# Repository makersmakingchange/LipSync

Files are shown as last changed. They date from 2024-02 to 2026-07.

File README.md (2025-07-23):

# LipSync

The LipSync is a mouth-operated sip-and-puff joystick that can emulate a mouse, wireless Bluetooth mouse, or gamepad. It enables people with disabilities that limit their mobility to control a computer, gaming console, smart phone, or tablet.

This most recent version, the LipSync 4.1, is made up of the LipSync Joystick and LipSync Hub. The Joystick is the primary user interface, and contains a low-force Hall-Effect joystick and sip and puff sensors. The Hub has a display that provides a graphical interface for independently adjusting settings, as well as it provides the connection to the host device and up to three external assistive switches with 3.5 mm jacks.

The device is comprised of off-the-shelf electronics and hardware, a custom PCB and 3D printed parts. The overall cost of materials (including materials required in bulk) for a single build is about $325 (plus shipping). In larger quantities, the cost of materials is closer to $175.

The LipSync is compatible with a range of host devices that are able to support a USB Mouse, a USB Gamepad and/or a Bluetooth Mouse. Compatible devices include PC and Mac computers and laptops, Android, iOS, and Windows smartphone and tablets, and the Xbox Adaptive Controller. 

The LipSync is Open Assistive Technology (OpenAT) and is certified as Open Source Hardware by the Open Source Hardware Association under the OSHWA UID [CA000046](https://certification.oshwa.org/ca000046.html). Under the terms of the open source hardware licenses, the LipSync may be built, used, and improved by anyone.  

Older versions of the LipSync are now obsolete. Documentation and design files are still available at the [LipSync Classic Repository.](https://github.com/makersmakingchange/OldLipSync)

The existing LipSync Interface Cable options in the BOM are not in stock. We are working on sourcing suitable alternatives.

Last updated: 2025-Jul-22

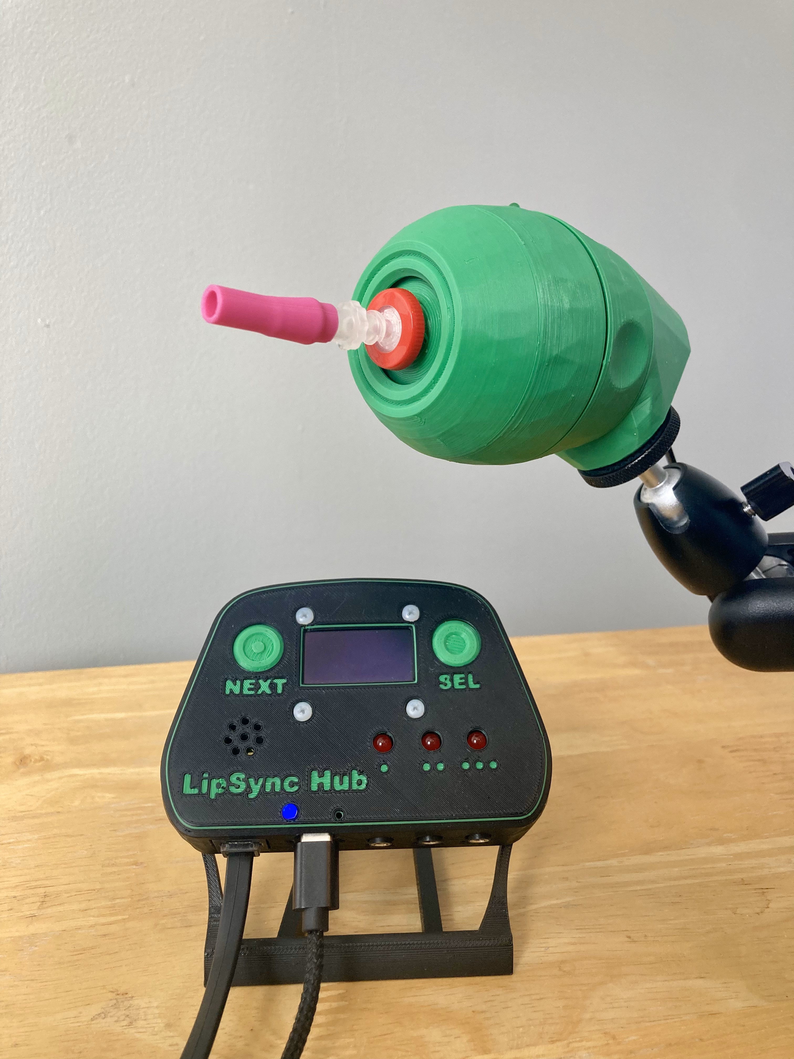
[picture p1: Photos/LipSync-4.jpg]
A green 3D-printed LipSync joystick with a pink sip-and-puff tube is mounted on an adjustable black arm. In front of it sits the LipSync Hub, a black and green control box with a small display screen, labeled buttons ('NEXT' and 'SEL'), indicator lights, and a USB cable connected at the bottom. Bot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


Makers Making Change Assistive Device Library Listing: [https://www.makersmakingchange.com/s/product/LipSync](https://www.makersmakingchange.com/s/product/lipsync/01tJR000000698fYAA)

## OpenAT Joysticks
This design is part of the [OpenAT Joystick Project](https://github.com/makersmakingchange/OpenAT-Joysticks), a collection of open source designs for digital access and adapted gaming. 

## How to Obtain the Device
### 1. Do-it-Yourself (DIY) or Do-it-Together (DIT)

This is an open-source assistive technology, so anyone is free to build it. All of the files and instructions required to build the device are contained within this repository. Refer to the Maker Guide below.

### 2. Request a build of this device

You may also submit a build request through the [MMC Library Page](https://www.makersmakingchange.com/s/product/LipSync/<mmc-salesforce-id>) to have a volunteer maker build the device. As the requestor, you are responsible for reimbursing the maker for the cost of materials and any shipping.

### 3. Build this device for someone else

If you have the skills and equipment to build this device, and would like to donate your time to create the device for someone who needs it, visit the [MMC Maker Wanted](https://makersmakingchange.com/maker-wanted/) section.

## Build Instructions

### 1. Read through the Maker Guide

The [Maker Guide](/Documentation/LipSync_Maker_Guide.pdf) contains all the necessary information to build this device, including tool lists, assembly instructions, programming instructions and testing instructions.

### 2. Order the Off-The-Shelf Components

The [Bill of Materials](/Documentation/LipSync_BOM.csv) lists all of the parts and components required to build the device. 

### 3. Print the 3D Printable components

All of the files and individual print files can be in the [/Build_Files/3D_Printing_Files](/Build_Files/3D_Printing_Files/) folder.

### 4. Assemble the LipSync

Reference the Assembly Guide section of the [Maker Guide](/Documentation/LipSync_Maker_Guide.pdf) for the tools and steps required to build each portion.

## How to improve this Device
As open source assistive technology, you are welcomed and encouraged to improve upon the design. 

## Files
### Documentation
| Document             | Version | Link                                                                     | Notes             |
|----------------------|---------|--------------------------------------------------------------------------|-------------------|
| Design Rationale     | 4.1     | [LipSync_Design_Rationale](/Documentation/LipSync_Design_Rationale.pdf)  |                   |
| Maker Guide          | 4.1     | [LipSync_Maker_Guide](/Documentation/LipSync_Maker_Guide.pdf)            |                   |
| Bill of Materials    | 4.1     | [LipSync_Bill_of_Materials](/Documentation/LipSync_BOM.csv)              |                   |
| User Guide           | 4.1     | [LipSync_User_Guide](/Documentation/LipSync_User_Guide.pdf)              |                   |
| Quickstart Guide     | 4.1     | [LipSync_Quickstart_Guide](/Documentation/LipSync_Quickstart_Guide.pdf)  |                   |
| Changelog            | 4.1     | [LipSync_Changelog](CHANGES.txt)                                         |                   |

### Design Files
 - [CAD Files](/Design_Files/CAD_Design_Files)
 - [PCB Files](/Design_Files/PCB_Design_Files)

### Build Files
 - [3D Printing Files](/Build_Files/3D_Printing_Files/)
 - [PCB Files](/Build_Files/PCB_Build_Files/)
 - [Firmware Files](/Build_Files/Firmware_Files)

## License
Copyright (c) 2024-2025 Neil Squire / Makers Making Change.

This repository describes Open Hardware:
 - Everything needed or used to design, make, test, or prepare the LipSync is licensed under the [CERN 2.0 Weakly Reciprocal license (CERN-OHL-W v2) or later](https://cern.ch/cern-ohl ) .
 - All software is under the [GNU General Public License v3.0 (GPL-3.0)](https://www.gnu.org/licenses/gpl.html).
 - Accompanying material such as instruction manuals, videos, and other copyrightable works that are useful but not necessary to design, make, test, or prepare the LipSync are published under a [Creative Commons Attribution-ShareAlike 4.0 license (CC BY-SA 4.0)](https://creativecommons.org/licenses/by-sa/4.0/) .

You may redistribute and modify this documentation and make products using it under the terms of the [CERN-OHL-W v2](https://cern.ch/cern-ohl).
This documentation is distributed WITHOUT ANY EXPRESS OR IMPLIED WARRANTY, INCLUDING OF MERCHANTABILITY, SATISFACTORY QUALITY AND FITNESS FOR A PARTICULAR PURPOSE.
Please see the CERN-OHL-W v2 for applicable conditions.

Source Location: https://github.com/makersmakingchange/LipSync

List of open source licenses. Hardware: CERN-OHL-W-2.0, Software: GPL-3.0-or-later, Documentation: CC-BY-SA-4.0.

## Attribution

The LipSync was designed by Neil Squire Society / Makers Making Change. The initial development of a 3D printable LipSync was supported by the Google Impact Challenge: Disabilities grant from Google.org. Further development was supported through the Government of Canada's Innovation Science and Economic Development [Accessible Technology Program](https://ised-isde.canada.ca/site/accessible-technology-program). These and other funders have also enabled Neil Squire / Makers Making Change to deploy numerous LipSyncs to users at reduced cost.

The latest design (V4.0) incorporates feedback and suggestions from numerous users, clinicians, and volunteer makers. In particular, 4.0.AlphaII was tested by the following users: Omar Al-azawi, Don Danbrook, Ean Price, Jim Ryan and Kaileen Selig.

V4.0 incorporates several commercially available open source hardware components:
 - [Adafruit TLV493D Triple-Axis Magnetometer - STEMMA QT / Qwiic](https://www.adafruit.com/product/4366). The PCB design is available under a CC-BY-SA 4.0 license at https://github.com/adafruit/Adafruit-TLV493D-PCB. 
 - [Adafruit LPS33HW Water Resistant Pressure Sensor - STEMMA QT](https://www.adafruit.com/product/4414). The PCB design is available under a CC-BY-SA 4.0 license at https://github.com/adafruit/Adafruit-LPS3X-PCB. 
 - [Adafruit LPS22 Pressure Sensor - STEMMA QT / Qwiic - LPS22HB](https://www.adafruit.com/product/4633). The PCB design is available under a CC-BY-SA 4.0 license at https://github.com/adafruit/Adafruit-LPS2X-PCB. 
 - [Adafruit 128X64 monochrome OLED Display Board](https://www.adafruit.com/product/938). The PCB design is available under a CC-BY-SA 4.0 license at https://github.com/adafruit/Adafruit-128x64-Monochrome-OLED-PCB.
 - [SparkFun Qwiic Adapter Board (DEV-14495)](https://www.sparkfun.com/products/14495). The PCB design is available under a CC-BY-SA 4.0 license at https://github.com/sparkfun/Qwiic_Adapter.   
 - [SparkFun RJ11 Breakout Board (BOB-14021)](https://www.sparkfun.com/products/14021). The PCB design is available under a CC-BY-SA 4.0 license at https://github.com/sparkfun/RJ11_Breakout. 

The LipSync firmware utilizes the Arduino development platform, an open-source electronics platform based on easy-to-use hardware and software. Arduino is developed and maintained by the Arduino community, and the project wouldn't be possible without their contributions.
Arduino is a registered trademark of Arduino AG. For more information about Arduino and to contribute to the community, visit the official Arduino website at www.arduino.cc.
The LipSync Firmware code uses several libraries:
 - [Adafruit_BusIO](https://github.com/adafruit/Adafruit_BusIO)  by Adafruit
 - [Adafruit_GFX](https://github.com/adafruit/Adafruit-GFX-Library) by Adafruit
 - [Adafruit_LPS2X](https://github.com/adafruit/Adafruit_LPS2X) by Adafruit
 - [Adafruit_LPS33HW](https://github.com/adafruit/Adafruit_LPS35HW) by Adafruit
 - [Adafruit_Sensor](https://github.com/adafruit/Adafruit_Sensor) by Adafruit
 - [Adafruit_SSD1306](https://github.com/adafruit/Adafruit_SSD1306) by Adafruit
 - [ArduinoJson](https://github.com/bblanchon/ArduinoJson) by Benoit Blanchon
 - [TLV493D-A1B6](https://github.com/Infineon/TLV493D-A1B6-3DMagnetic-Sensor) by Infineon Technologies

### Contributors
Designers:
 
 - Derrick Andrews, Neil Squire Society / Makers Making Change.
 - Stephan Dobri, Neil Squire Society / Makers Making Change.
 - Tyler Fentie, Neil Squire Society / Makers Making Change.
 - Milad Hajihassan, Neil Squire Society / Makers Making Change.
 - Jake McIvor, Neil Squire Society / Makers Making Change.
 - Stephen Moyer, Neil Squire Society / Makers Making Change.
 - Brad Wellington, Neil Squire Society / Makers Making Change.
 - Josie Versloot, Neil Squire Society / Makers Making Change.
 
## Open Source Hardware Certification

The LipSync has been certified as open source hardware by the Open Source Hardware Association under the OSHWA UID [CA000046](https://certification.oshwa.org/ca000046.html).

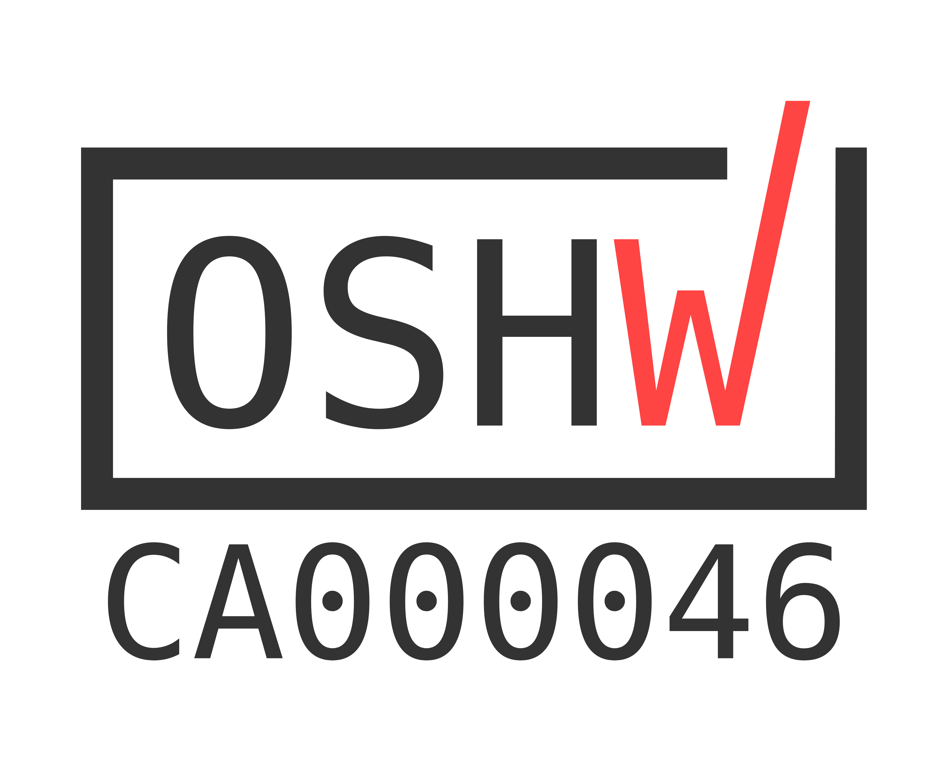
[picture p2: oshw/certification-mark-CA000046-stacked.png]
Open Source Hardware Certification Mark for LipSync: CA000046


---

## About Makers Making Change
[Makers Making Change Logo](https://www.makersmakingchange.com/)

Makers Making Change is a program of [Neil Squire](https://www.neilsquire.ca/), a Canadian non-profit that uses technology, knowledge, and passion to empower people with disabilities.

Makers Making Change leverages the capacity of community based Makers, Disability Professionals and Volunteers to develop and deliver affordable Open Source Assistive Technologies.

 - Website: [www.MakersMakingChange.com](https://www.makersmakingchange.com/)
 - GitHub: [makersmakingchange](https://github.com/makersmakingchange)
 - Twitter: [@makermakechange](https://twitter.com/makermakechange)
 - Instagram: [@makersmakingchange](https://www.instagram.com/makersmakingchange)
 - Facebook: [makersmakechange](https://www.facebook.com/makersmakechange)
 - LinkedIn: [Neil Squire Society](https://www.linkedin.com/company/neil-squire-society/)
 - Thingiverse: [makersmakingchange](https://www.thingiverse.com/makersmakingchange/about)
 - Printables: [MakersMakingChange](https://www.printables.com/@MakersMakingChange)

### Contact Us
For technical questions, to get involved, or to share your experience we encourage you to [visit our website](https://www.makersmakingchange.com/) or [contact us](https://www.makersmakingchange.com/s/contact).

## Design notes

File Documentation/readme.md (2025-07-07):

This folder contains the documentation for the LipSync. Editable versions of the documentation are located in the [Working_Documents](Documentation/Working_Documents) folder.

# Quick Links
Arduino IDE Board files for Seeed XIAO nRF52840: https://files.seeedstudio.com/arduino/package_seeeduino_boards_index.json

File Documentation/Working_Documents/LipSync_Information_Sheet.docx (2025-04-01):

# Contents

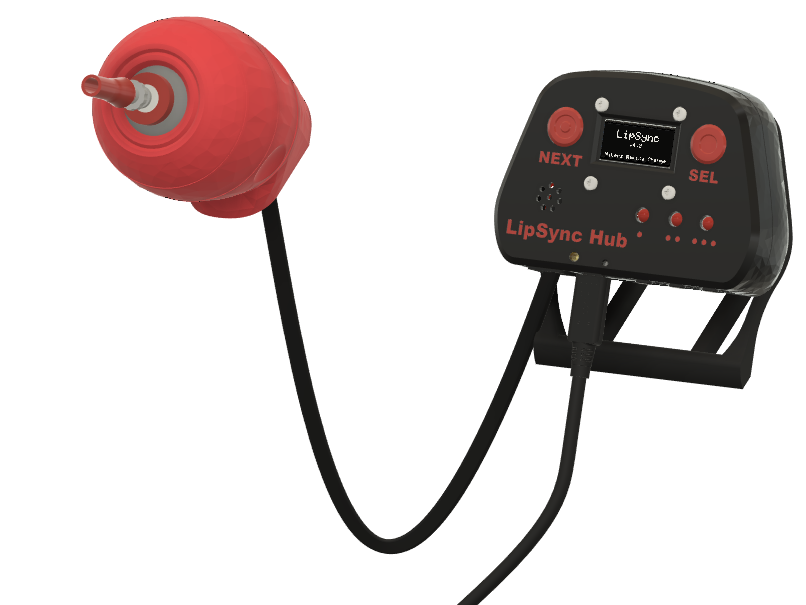
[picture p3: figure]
Numbered diagram of LipSync Setup
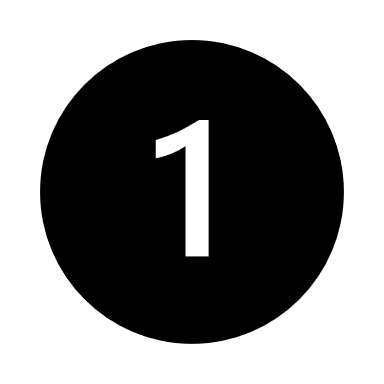
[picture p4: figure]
Badge 1 with solid fill
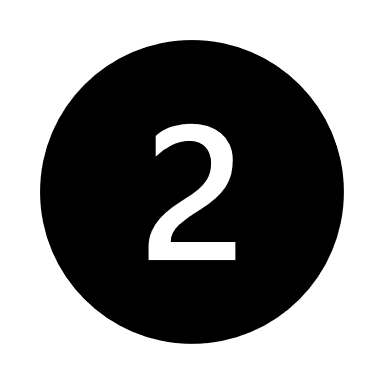
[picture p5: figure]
Badge with solid fill
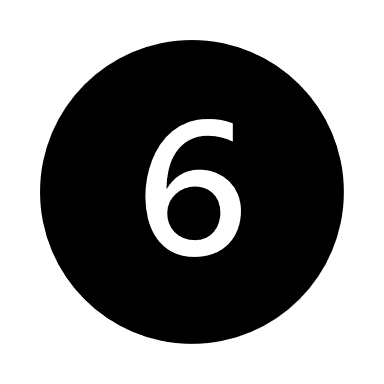
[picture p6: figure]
Badge 6 with solid fill
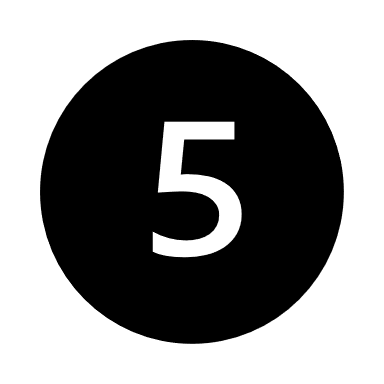
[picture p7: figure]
Badge 5 with solid fill
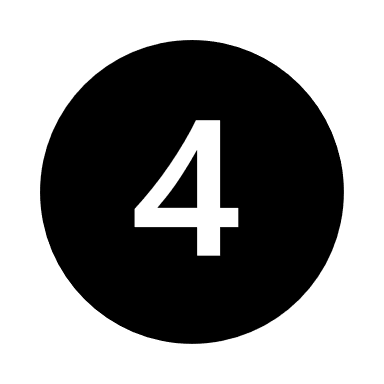
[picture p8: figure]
Badge 4 with solid fill
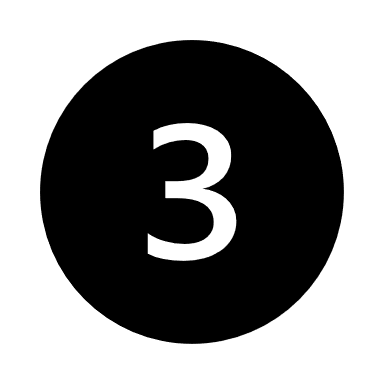
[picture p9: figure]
Badge 3 with solid fill

ID Part QTY 1 LipSync Joystick 1 2 LipSync Hub 1 3 LipSync Interface Cable 1 4 LipSync Hub Stand 1 5 LipSync Mouthpieces 5 6 USB-C – USB-A Cable 1

# Setup Instructions

1. Mount the LipSync Joystick.
2. Mount the Hub on the Hub Stand.
3. Connect the Joystick to the Hub using the Interface Cable.
4. Attach a mouthpiece to the Joystick.
5. Connect the Hub to the Host Device using a USB Cable.

# Additional Documentation

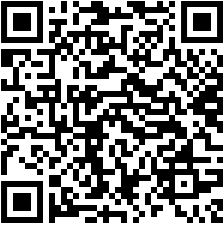
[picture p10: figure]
LipSync Quickstart Guide PDF QR Code
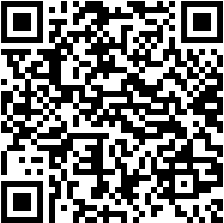
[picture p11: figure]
LipSync User Guide PDF QR Code

Quickstart Guide (https://github.com/makersmakingchange/LipSync/blob/main/Documentation/LipSync_Quickstart_Guide.pdf) | User Guide (https://github.com/makersmakingchange/LipSync/blob/main/Documentation/LipSync_User_Guide.pdf)

© 2024-2025 Neil Squire Society. This work is licensed under the CC BY SA 4.0 License: http://creativecommons.org/licenses/by-sa/4.0 Files available at https://github.com/makersmakingchange/LipSync Page 1 of 1

V4.1 | MARCH 2025 LipSync INFORMATION SHEET

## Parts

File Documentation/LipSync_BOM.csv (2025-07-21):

 | LipSync |  |  |  |  |  |  | Total filament (g) |  |  | Unit Cost | Total Cost | Total Print time (hr)
 | Version: | 4.1 |  | Last updated: | 2025-Mar-21 |  |  | 158 |  |  | $176.11 | $295.70 | 15:03
 | Commercial Parts
ID | Part | Description |  | Manufacturer | Supplier | Supplier PN | QTY | QTY / PKG | PKGs | $/PKG | Price per Unit | Total Price |  | Link | Alternate
Joystick Parts
U2 | TLV493D | Adafruit TLV493D Triple-Axis Magnetometer - STEMMA QT / Qwiic | Joystick | Adafruit | Digikey | 1528-4366-ND | 1 | 1 | 1 | $8.53 | $8.53 | $8.53 |  | https://www.digikey.ca/en/products/detail/adafruit-industries-llc/4366/10481837
U3 | LPS33HW | Adafruit LPS33HW Water Resistant Pressure Sensor - STEMMA QT | Joystick | Adafruit | Digikey | 1528-4414-ND | 1 | 1 | 1 | $17.91 | $17.91 | $17.91 |  | https://www.digikey.ca/en/products/detail/adafruit-industries-llc/4414/11201428
U4 | LPS22 | Adafruit LPS22 Pressure Sensor - STEMMA QT / Qwiic - LPS22HB | Joystick | Adafruit | Digikey | 1528-4633-ND | 1 | 1 | 1 | $9.96 | $9.96 | $9.96 |  | https://www.digikey.ca/en/products/detail/adafruit-industries-llc/4633/12396897
BRG | Bearing | 0.250" ball bearing, 1/4" ID, 0.5" OD | Joystick | Mechatronics Bearing Group | Digikey | 1995-1003-ND | 4 | 1 | 4 | $3.41 | $13.64 | $13.64 |  | https://www.digikey.ca/en/products/detail/mechatronics-bearing-group/DDRI814ZZRA3P25LY121/9608362
MAG | Magnet | Cylindrical magnet, 8 mm OD, 2.5 mm thick | Joystick | Radial Magnet, Inc. | Digikey | 469-1029-ND | 3 | 1 | 3 | $1.18 | $3.54 | $3.54 |  | https://www.digikey.ca/en/products/detail/radial-magnets-inc/9029/5218824
CBL-QWIIC-150-M | QWIIC-150 to Male Headers | JST SH 4-PIN TO PREMIUM MALE HEA | Joystick | Adafruit | Digikey | 1528-4209-ND | 1 | 1 | 1 | $1.39 | $1.39 | $1.39 |  | https://www.digikey.ca/en/products/detail/adafruit-industries-llc/4209/10230003
CBL-QWIIC-50 | QWIIC-50 | Qwiic JST SH 4-pin Cable - 50mm | Joystick | SparkFun Electronics | Digikey | 1568-PRT-17260-ND | 1 | 1 | 1 | $1.52 | $1.52 | $1.52 |  | https://www.digikey.ca/en/products/detail/sparkfun-electronics/PRT-17260/13629028
CBL-QWIIC-200 | QWIIC-200 | Qwiic Cable JST SH 4-pin Cable - 200mm | Joystick | SparkFun Electronics | Digikey | 1568-PRT-17258-ND‎ | 1 | 1 | 1 | $2.48 | $2.48 | $2.48 |  | https://www.digikey.ca/en/products/detail/sparkfun-electronics/PRT-17258/13629029?s=N4IgTCBcDaIAoCUAqBaAjAdjAVgBwgF0BfIA
PCB2 | RJ11 Breakout board | RJ11 Breakout | Joystick | SparkFun Electronics | Digikey | 1568-1440-ND | 1 | 2 | 1 | $3.01 | $1.51 | $3.01 |  | https://www.digikey.ca/en/products/detail/sparkfun-electronics/BOB-14021/6228638
CBL-RJ11 | RJ11 cable | Modular Cable Plug to Plug 6p6c (RJ11, RJ12, RJ14, RJ25) 7.00' (2.13m) Unshielded | Joystick Cable | Assmann WSW Components | Digikey | A2662R-07-ND | 1 | 1 | 1 | $3.94 | $3.94 | $3.94 |  | https://www.digikey.ca/en/products/detail/assmann-wsw-components/AT-S-26-6-6-B-7-R/1972588
J1 | Modular Connector Jack | Jack Modular Connector 6p6c (RJ11, RJ12, RJ14, RJ25) 90° Angle (Right) Unshielded Cat3 | Joystick | TE Connectivity AMP Connectors | Digikey | A31422-ND | 2 | 1 | 2 | $1.45 | $2.90 | $2.90 |  | https://www.digikey.ca/en/products/detail/te-connectivity-amp-connectors/5555165-1/769566
- | Male Luer Connectors | Mouthpiece Connector to Gimbal | Joystick |  | Amazon | B13193 | 1 | 30 | 1 | $11.99 | $0.40 | $11.99 |  | https://www.amazon.ca/gp/product/B0B8CJVX3S
- | Silicone Tubing, 2 mm ID, 4 mm OD | Air path to sensor | Joystick |  | Amazon |  | 50 | 3000 | 1 | $12.49 | $0.21 | $12.49 |  | https://www.amazon.ca/gp/product/B01C3GCZTM
Hub Parts
CBL-QWIIC-100 | QWIIC-100 | Qwiic JST SH 4-pin Cable - 100 mm | Hub | Adafruit | Digikey | 1528-4210-ND | 1 | 1 | 1 | $1.39 | $1.39 | $1.39 |  | https://www.digikey.ca/en/products/detail/adafruit-industries-llc/4210/10230021
U1 | Seeed Studio Xiao nrf52840 | Microcontroller | Hub | Seeed Studio Technology Co., Ltd. | Digikey | 1597-102010448-ND | 1 | 1 | 1 | $15.85 | $15.85 | $15.85 |  | https://www.digikey.ca/en/products/detail/seeed-technology-co.,-ltd/102010448/16652893
J6 | Male Headers for Xiao | 7-pin male headers for microcontroller | Hub | Seeed Studio Technology Co., Ltd. | Digikey | 1597-102010490-ND | 2 | 5 | 1 | $0.37 | $0.15 | $0.37 |  | https://www.digikey.ca/en/products/detail/seeed-technology-co-ltd/102010490/19176770
SW1/SW2/SW3 | Mono Switch Jacks | Mono switch jacks | Hub | CUI Devices | Digikey | CP1-3535NG-ND | 3 | 1 | 3 | $2.29 | $6.87 | $6.87 |  | https://www.digikey.ca/en/products/detail/cui-devices/SJ1-3535NG/738699
S1/S2 | Tactile switches | Tactile switches for controls | Hub | Omron | Digikey | SW801-ND | 2 | 1 | 2 | $1.02 | $2.04 | $2.04 |  | https://www.digikey.ca/en/products/detail/omron-electronics-inc-emc-div/B3F-5050/368377
J5 | 7 Pin Female Headers | 7 position female headers | Hub | Sullins Connector Solutions | Digikey | S7005-ND | 2 | 1 | 2 | $0.88 | $1.76 | $1.76 |  | https://www.digikey.ca/en/products/detail/sullins-connector-solutions/PPTC071LFBN-RC/810146
J2 | 4 Pin Male Headers | 4 Pin Male Headers | Hub | Sullins Connector Solutions | Digkey | S1011EC-04-ND | 1 | 1 | 1 | $0.19 | $0.19 | $0.19 |  | https://www.digikey.ca/en/products/detail/sullins-connector-solutions/PRPC004SAAN-RC/2775250
DISP | LCD feedback screen | Monochrome 1.3" 128x64 OLED graphic display - STEMMA QT / Qwiic | Hub | Adafruit | Digikey | 1528-1512-ND | 1 | 1 | 1 | $30.47 | $30.47 | $30.47 |  | https://www.digikey.ca/en/products/detail/adafruit-industries-llc/938/5774238
LS1 | Buzzer PS1240 | Piezo Buzzer PS1240 | Hub | TDK | Digikey | 445-2525-1-ND - Cut Tape (CT) | 1 | 1 | 1 | $0.92 | $0.92 | $0.92 |  | https://www.digikey.ca/en/products/detail/tdk-corporation/PS1240P02BT/935924
D1/D2/D3 | 5MM Red LED | Diffused 5MM Round T/H Red LED | Hub | Würth Elektronik | Digikey | 732-5016-ND | 3 | 1 | 3 | $0.26 | $0.78 | $0.78 |  | https://www.digikey.ca/en/products/detail/w%C3%BCrth-elektronik/151051RS11000/4490012
R2/R3/R4 | LED Resistors | 68 Ohm Resistor, 1/4W | Hub | YAGEO | Digikey | 68QBK-ND | 3 | 1 | 3 | $0.16 | $0.48 | $0.48 |  | https://www.digikey.ca/en/products/detail/yageo/CFR-25JB-52-68R/2832
R1 | Speaker Resistor | 100 Ohm Resistor | Hub | YAGEO | Digikey | 100XBK-ND | 1 | 1 | 1 | $0.14 | $0.14 | $0.14 |  | https://www.digikey.ca/en/products/detail/yageo/MFR-25FBF52-100R/12795
C1 | Capacitor | 10 µF Ceramic Capacitor | Hub | KEMET | Digikey | C430C106K3R5TA-ND | 1 | 1 | 1 | $1.01 | $1.01 | $1.01 |  | https://www.digikey.ca/en/products/detail/kemet/C430C106K3R5TA/6685941
J4 | Qwiic Adapter Board | Sparkfun Qwiic Adapter | Hub | SparkFun Electronics | Digikey | 1568-1785-ND | 1 | 1 | 1 | $2.34 | $2.34 | $2.34 |  | https://www.digikey.ca/en/products/detail/sparkfun-electronics/DEV-14495/7942483
M2.5n | M2.5 Nut | HEX NUT, NATURAL, NYLON, M2.5 X | Hub + Joystick | Essentra Components | Digikey | 04M025045HN | 7 | 1 | 7 | $0.19 | $1.33 | $1.33 |  | https://www.digikey.ca/en/products/detail/essentra-components/04M025045HN/9677099
M2.5x8 | M2.5 Screw - 8 mm length | PAN PHILLIPS SCREW, M2.5X0.45 T x 8 mm Long | Hub + Joystick | Essentra Components | Digikey | 50M025045P008 | 7 | 1 | 7 | $0.20 | $1.40 | $1.40 |  | https://www.digikey.ca/en/products/detail/essentra-components/50M025045P008/11638585
LP | Light Pipe 0.250" | Light Pipe | Hub + Joystick | Dialight | Digikey | 350-3746-ND | 2 | 1 | 2 | $1.66 | $3.32 | $3.32 |  | https://www.digikey.ca/en/products/detail/dialight/51513030250F/4965201
No4x3_8 | No.4 Screw x 3/8in | SHT MTL SCREW PAN PHIL #4 | Hub + Joystick | Serpac | Digikey | SR6005-ND | 8 | 1 | 8 | $0.63 | $5.04 | $5.04 |  | https://www.digikey.ca/en/products/detail/serpac/6005/307599
- | T-Nut | 1/4-20 T-nut x 5/16" length | Hub + Joystick | PowerTec | Amazon | ‎QTN1110 | 2 | 50 | 1 | $15.54 | $0.62 | $15.54 |  | https://www.amazon.ca/gp/product/B07NCXNKJR
CBL-USB | USB C cable - 6 ft | USB C to USB A cable for microcontroller | Hub Cable | Amazon | Amazon |  | 1 | 1 | 1 | $12.95 | $12.95 | $12.95 |  | https://www.amazon.ca/dp/B01GGKYN0A
Mouthpiece Parts
 | Silicone Straw | Mouthpiece Tip | Mouthpiece Consumable | WOVTE | Amazon |  | 2 | 6 | 1 | $12.49 | $4.16 | $12.49 |  | https://www.amazon.ca/WOVTE-Reusable-Toddlers-Silicone-Cleaning/dp/B07KVTYG5X
 | Female Luer Lock 1/4 Inch Luer Lock Connector Kit to Syringe Coupler Adapter | Mouthpiece Tip Adapter | Mouthpiece Consumable | PEUTIER | Amazon | B0CJY11V4B | 5 | 30 | 1 | $10.99 | $1.83 | $10.99 |  | https://www.amazon.ca/dp/B0CJY11V4B
- | Syringe Filters | Mouthpiece Filter | Mouthpiece Consumable |  | Amazon | B0BKRR426C | 6 | 100 | 1 | $39.99 | $2.40 | $39.99 |  | https://www.amazon.ca/gp/product/B0BKRR426C
 | Custom PCB
 | Part | Description |  | Manufacturer | Supplier | Supplier PN | QTY | QTY / PKG | PKG | $/PKG | Price per Unit | Total Price |  | Link
PCB1 | LipSync Hub PCB | PCB | Hub | JLCPCB |  |  | 1 | 5 | 1 | 5 | 1 | 5 |  | https://jlcpcb.com/
 | PCB Shipping | PCB Shipping - DHL Express | Shipping |  |  |  | 1 | 5 | 1 | 25 | 5 | 25
 | PCB Shipping | PCB Shipping - Fedex International | Shipping |  |  |  | 0 | 5 | 0 | 25 | 0 | 0
 | 3D Printed Parts ESTIMATED PRICING USING 1KG ROLL COST: | $30.00
 | Part | Description |  |  |  |  | QTY | Mass (g) |  | Estimated Price | Estimated Price | Estimated Price | Print Time (hr:Min) | Link
 | LS4_Hub_Top | Top of the Hub | Hub |  |  |  | 1 | 19 |  | $0.57 | $0.57 | $0.57 | 0:36
 | LS4_Hub_Bottom | Bottom of the Hub | Hub |  |  |  | 1 | 26 |  | $0.78 | $0.78 | $0.78 | 1:12
 | LS4_Hub_LED_Spacer | Spacer to properly position feedback LEDs in the Hub | Hub |  |  |  | 1 | 2 |  | $0.06 | $0.06 | $0.06 | 1:34
 | LS4_Hub_Next_Button | Button to push an internal switch on the Hub | Hub |  |  |  | 1 | 2 |  | $0.06 | $0.06 | $0.06 | 2:07
 | LS4_Hub_Select_Button | Button to push an internal switch on the Hub | Hub |  |  |  | 1 | 2 |  | $0.06 | $0.06 | $0.06 | 0:13
 | LS4_Inner_Gimbal_1 | Half of the inner gimbal mechanism | Joystick |  |  |  | 1 | 3 |  | $0.09 | $0.09 | $0.09 | 0:11
 | LS4_Inner_Gimbal_ 2 | Half of the inner gimbal mechanism | Joystick |  |  |  | 1 | 3 |  | $0.09 | $0.09 | $0.09 | 0:11
 | LS4_Outer_Gimbal_1 | Half of the outer gimbal mechanism | Joystick |  |  |  | 1 | 3 |  | $0.09 | $0.09 | $0.09 | 0:19
 | LS4_Outer_ Gimbal_2 | Half of the outer gimbal mechanism | Joystick |  |  |  | 1 | 3 |  | $0.09 | $0.09 | $0.09 | 0:19
 | LS4_Gimbal_Shield | Cover for the front of the gimbal mechanism | Joystick |  |  |  | 1 | 4 |  | $0.12 | $0.12 | $0.12 | 0:18
 | LS4_Magnet_Clip | Piece to hold the magnets of the gimbal sled in place | Joystick |  |  |  | 2 | 1 |  | $0.03 | $0.03 | $0.03 | 0:02
 | LS4_Gimbal_Sled | Sled to hold gimbal mechanism and insert into the housing | Joystick |  |  |  | 1 | 5 |  | $0.15 | $0.15 | $0.15 | 0:43
 | LS4_Front_Cap | Front face of the joystick enclosure | Joystick |  |  |  | 1 | 14 |  | $0.42 | $0.42 | $0.42 | 0:58
 | LS4_Joystick_Housing | Main body of the joystick enclosure | Joystick |  |  |  | 1 | 26 |  | $0.78 | $0.78 | $0.78 | 2:05
 | LS4_Outer_Locking_Ring | Outer ring used to lock the joystick orientation in place | Joystick |  |  |  | 1 | 17 |  | $0.51 | $0.51 | $0.51 | 1:15
 | LS4_Inner_Locking_Ring | Inner ring that helps lock the joystick orientation in place | Joystick |  |  |  | 1 | 6 |  | $0.18 | $0.18 | $0.18 | 0:33
 | LS4_Rear_Housing | Back portion of the joystick enclosure | Joystick |  |  |  | 1 | 22 |  | $0.66 | $0.66 | $0.66 | 2:27
 | Alternatives
 | Part | Description |  | Manufacturer | Supplier
 | TLV493D | Adafruit TLV493D Triple-Axis Magnetometer - STEMMA QT / Qwiic |  | Adafruit | Mouser | 485-4366 | 1 | 1 | 1 | $8.63 | $8.63 | $8.63 |  | https://www.mouser.ca/ProductDetail/Adafruit/4366?qs=Cb2nCFKsA8rqS%252BdmeewMYw%3D%3D
 | LPS33HW | Adafruit LPS33HW Water Resistant Pressure Sensor - STEMMA QT |  | Adafruit | Mouser | 485-4414 | 1 | 1 | 1 | $18.13 | $18.13 | $18.13 |  | https://www.mouser.ca/ProductDetail/Adafruit/4414?qs=xZ%2FP%252Ba9zWqbFiAS6M6RHZw%3D%3D
 | LPS22 | Adafruit LPS22 Pressure Sensor - STEMMA QT / Qwiic - LPS22HB |  | Adafruit | Mouser | 485-4633 | 1 | 1 | 1 | $10.08 | $10.08 | $10.08 |  | https://www.mouser.ca/ProductDetail/Adafruit/4633?qs=W%2FMpXkg%252BdQ4ebNdNVsYA5Q%3D%3D
CBL-QWIIC-100 | QWIIC-100 | Qwiic JST SH 4-pin Cable - 100mm |  | Adafruit | Mouser | 485-4210 | 1 | 1 | 1 | $1.38 | $1.38 | $1.38 |  | https://www.mouser.ca/ProductDetail/Adafruit/4210?qs=PzGy0jfpSMuCfezrcTX9rQ%3D%3D
CBL-QWIIC-50 | QWIIC-50 | Qwiic JST SH 4-pin Cable - 50mm |  | Adafruit | Mouser | 485-4399 | 1 | 1 | 1 | $1.38 | $1.38 | $1.38 |  | https://www.mouser.ca/ProductDetail/Adafruit/4399?qs=xZ%2FP%252Ba9zWqZ%2FTpT35o5XxA%3D%3D
CBL-QWIIC-50 | QWIIC-50 | Qwiic JST SH 4-pin Cable - 50mm |  | SparkFun Electronics | PiShop |  | 1 | 1 | 1 | $1.95 | $1.95 | $1.95 |  | https://www.pishop.ca/product/stemma-qt-qwiic-jst-sh-4-pin-cable-50mm-long/
 | C1 Capacitor | 10 µF Ceramic Capacitor |  | TDK Corporation | Digikey | 445-181284-1-ND | 1 | 1 | 1 | $0.72 | $0.72 | $0.72 |  | https://www.digikey.ca/en/products/detail/tdk-corporation/FG28X5R1E106MRT06/10185405
 | RJ11 Breakout board | RJ11 Breakout |  | SparkFun Electronics | Mouser | 474-BOB-14021 | 1 | 1 | 1 | $2.83 | $2.83 | $2.83 |  | https://www.mouser.ca/ProductDetail/SparkFun/BOB-14021?qs=FNcb6ahWXRxYfdHxmKm33A%3D%3D
 | RJ11 Jack | Jack Modular Connector 6p6c (RJ11, RJ12, RJ14, RJ25) 90° Angle (Right) Unshielded Cat3 |  | TE Connectivity AMP Connectors | Mouser | 571-5555165-1 | 2 | 1 | 2 | $1.46 | $2.92 | $2.92 |  | https://www.mouser.ca/ProductDetail/TE-Connectivity-AMP/5555165-1?qs=BcfjnG7NVaWb2UIqidZ6Zg%3D%3D
 | RJ11 cable | Modular Cable Plug to Plug 6p6c (RJ11, RJ12, RJ14, RJ25) 7.00' (2.13m) Unshielded |  | Amphenol Cables on Demand | Mouser | MP-5FRJ11STWS-007 | 1 | 1 | 1 | $5.34 | $5.34 | $5.34 |  | https://www.mouser.ca/ProductDetail/Amphenol-Cables-on-Demand/MP-5FRJ11STWS-007?qs=H5r6JxgcqAhybXCGFpSfXQ%3D%3D
 | RJ11 cable | Modular Cable Plug to Plug 6p6c (RJ11, RJ12, RJ14, RJ25) 7.00' (2.13m) Unshielded |  | CNC Tech | Digikey | 1175-2331-ND | 1 | 1 | 1 | $6.40 | $6.40 | $6.40
 | Mono switch jacks | Mono switch jacks |  | CUI Devices | Mouser | 490-SJ1-3535NG | 3 | 1 | 3 | $2.31 | $6.93 | $6.93 |  | https://www.mouser.ca/ProductDetail/CUI-Devices/SJ1-3535NG?qs=WyjlAZoYn50jUmKVsqeRJw%3D%3D
 | 5MM Red LED | Diffused 5MM Round T/H Red LED |  | Kingbright | Digikey | 754-1732-ND | 2 | 1 | 2 | $0.89 | $1.78 | $1.78 |  | https://www.digikey.ca/en/products/detail/kingbright/WP7113ID5V/3084220
 | Xiao nRF52840 | Microcontroller | Hub | Seeed Studio | Mouser |  | 1 | 1 | 1 | $0.89 | $0.89 | $0.89 |  | https://www.mouser.ca/ProductDetail/Seeed-Studio/102010448?qs=Znm5pLBrcAJ5g%252BWAkitg4w%3D%3D
 | M2.5 Bolt | M2.5 Bolt | Hub + Joystick | Essentra | Mouser | 144-50M025045K008 | 6 | 1 | 6 | $0.09 | $0.01 | $0.52 |  | https://www.mouser.ca/ProductDetail/Essentra/50M025045K008?qs=PzGy0jfpSMt5PUju15hdzg%3D%3D
 | M2.5 Nut | M2.5 Nut | Hub + Joystick | Essentra | Digikey | RPC7085-ND | 6 | 1 | 6 | $0.20 | $0.03 | $1.20 |  | https://www.digikey.ca/en/products/detail/essentra-components/04M025045HN/9677099
 | Buzzer | Piezo Buzzer | Hub | TDK Corporation | Digikey | 445-2525-1-ND | 1 | 1 | 1 | $0.96 | $0.96 | $0.96
 | Mouser Shipping |  |  |  | Mouser |  | 1 | 1 | 1 | $20.00 | $20.00 | $20.00
U2 | TLV493D | Adafruit TLV493D Triple-Axis Magnetometer - STEMMA QT / Qwiic | Joystick | Adafruit | Adafruit | 4366 | 1 | 1 | 1 |  | $- | $- |  | https://www.adafruit.com/product/4366
U3 | LPS33HW | Adafruit LPS33HW Water Resistant Pressure Sensor - STEMMA QT | Joystick | Adafruit | Adafruit | 4414 | 1 | 1 | 1 |  | $- | $- |  | https://www.adafruit.com/product/4414
U4 | LPS22 | Adafruit LPS22 Pressure Sensor - STEMMA QT / Qwiic - LPS22HB | Joystick | Adafruit | Adafruit | 4633 | 1 | 1 | 1 |  | $- | $- |  | https://www.adafruit.com/product/4633
CBL-QWIIC-50 | QWIIC-50 | Qwiic JST SH 4-pin Cable - 50mm |  | Adafruit | Adafruit | 4399 | 1 | 1 | 1 |  | $- | $- |  | https://www.adafruit.com/product/4399
CBL-QWIIC-100 | QWIIC-100 | Qwiic JST SH 4-pin Cable - 100mm |  | Adafruit | Adafruit | 4210 | 1 | 1 | 1 |  | $- | $- |  | https://www.adafruit.com/product/4210
CBL-QWIIC-150 | QWIIC-150-Male | Qwiic JST SH 4-pin Cable to Dupont - 150mm |  | Adafruit | Adafruit | 4209 | 1 | 1 | 1 |  | $- | $- |  | https://www.adafruit.com/product/4209
DISP | LCD feedback screen | Monochrome 1.3" 128x64 OLED graphic display - STEMMA QT / Qwiic | Hub | Adafruit | Digikey | 938 | 1 | 1 | 1 |  | $- | $- |  | https://www.adafruit.com/product/938#technical-details
 | Tactile Switch | Tactile Switch Buttons (12mm square, 6mm tall) | Hub | Adafruit | Adafruit | 1119 | 2 | 10 | 1 |  | $- | $- |  | https://www.adafruit.com/product/1119
 |  |  |  |  |  |  |  |  |  |  | $- | $-
PCB2 | RJ11 Breakout board | RJ11 Breakout | Joystick | SparkFun Electronics | SparkFun |  | 1 | 2 | 1 |  | $- | $- |  | https://www.sparkfun.com/products/14021
J4 | Qwiic Adapter Board | Sparkfun Qwiic Adapter | Hub | SparkFun Electronics | SparkFun | DEV014495 | 1 | 1 | 1 |  | $- | $- |  | https://www.sparkfun.com/products/14495
 |  |  |  |  |  |  |  |  | 0 |  | $- | $-
 | Syringe Filter | Filter | Mouthpiece Consumable | REKORI | Amazon |  | 6 | 100 | 1 | 43.31 | $2.60 | $43.31 |  | https://www.amazon.ca/Hydrophobic-Membrane-Filtration-Non-Sterile-Injection/dp/B0B9X33SHM
 | Silicone Straw | Mouthpiece Tip | Mouthpiece Consumable | LIFNY | Amazon |  | 2 | 12 | 1 | 13.99 | $2.33 | $13.99 |  | https://www.amazon.ca/Reusable-Silicone-Drinking-Approved-Tumblers/dp/B07PZTWW55
 | Female Luer Lock 1/4 Inch Luer Lock Connector Kit to Syringe Coupler Adapter | Mouthpiece Tip Adapter | Mouthpiece Consumable | MycologyLids | Amazon |  | 5 | 10 | 1 | 20.27 | $10.14 | $20.27 |  | https://www.amazon.ca/Female-Connector-6-4mm-Tubing-Adapter/dp/B0D7TW5R71
 | Silicone Tube | Silicone Tube | Mouthpiece Consumable | Kingsrey | Amazon |  | 3 | 500 | 1 | 16.36 | $0.10 | $16.36 |  | https://www.amazon.ca/Silicone-Thickness-Flexible-Transfer-Engraving/dp/B07X5VYDZK?sp_csd=d2lkZ2V0TmFtZT1zcF9hdGY
 | Male Luer lock x 1/8" Barb | Luer Lock connectors | Mouthpiece Consumable | RSN | Amazon |  | 1 | 10 | 1 | 12.31 | $1.23 | $12.31 |  | https://www.amazon.ca/RSN-Lab-3-2Mm-Adapter-Black/dp/B08414Q7JK
 |  |  |  |  |  |  |  |  | 0 |  | $- | $-
 |  |  |  |  |  |  |  |  | 0 |  | $- | $-

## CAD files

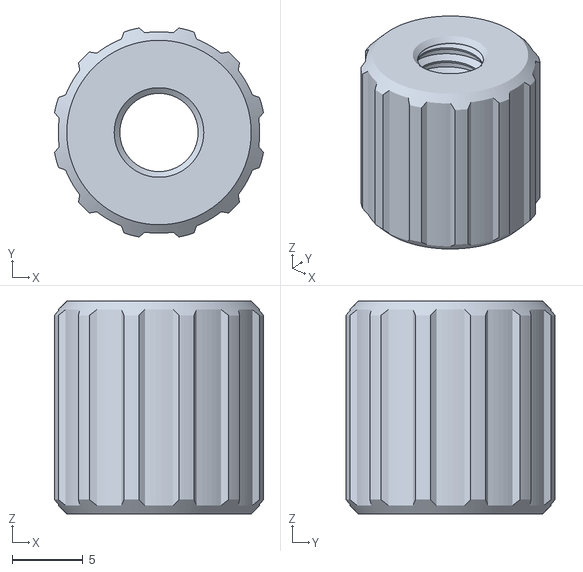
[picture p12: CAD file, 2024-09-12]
Build_Files/3D_Printing_Files/LS4_Hub/LS4_Hub_Stand/LipSync Hub Modular Mounting System/Build Files/PrintableKnob.stl
14.7 x 14.7 x 15.0

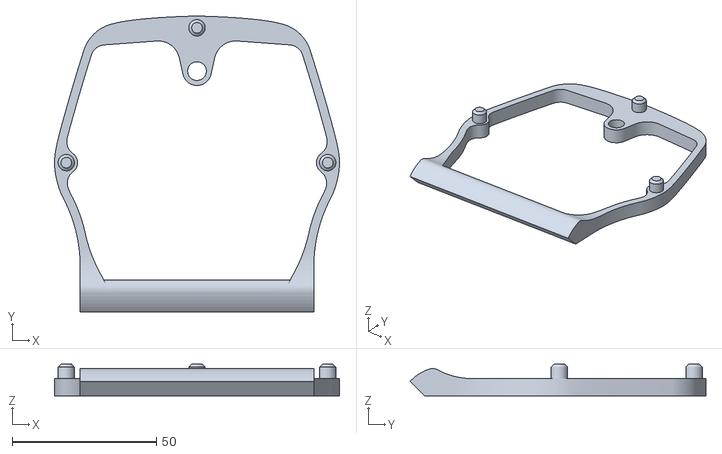
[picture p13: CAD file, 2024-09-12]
Build_Files/3D_Printing_Files/LS4_Hub/LS4_Hub_Stand/LS4_Hub_Stand_Front.stl
98.8 x 102.6 x 11.0

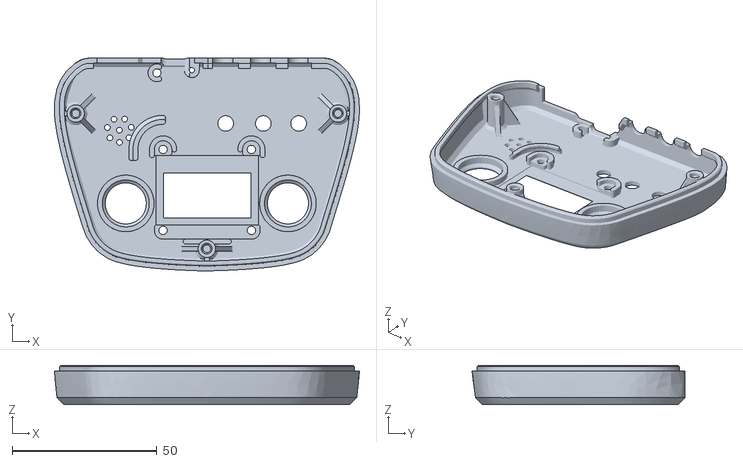
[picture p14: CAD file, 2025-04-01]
Build_Files/3D_Printing_Files/LS4_Hub/LS4_Hub_Top.stl
105.3 x 73.5 x 13.5

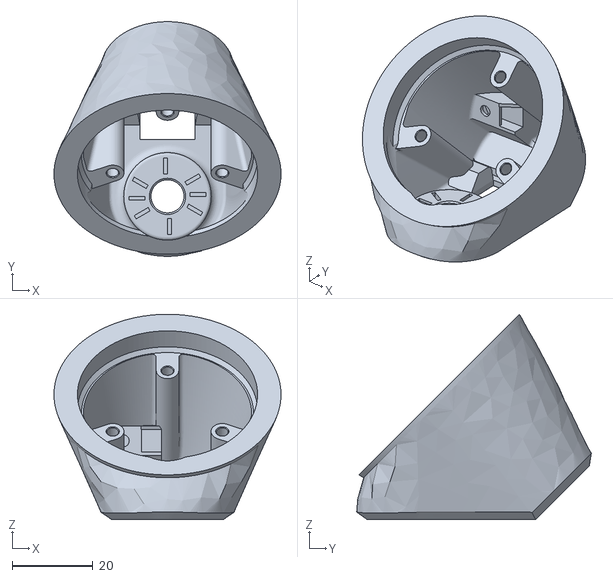
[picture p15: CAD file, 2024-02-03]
Build_Files/3D_Printing_Files/LS4_Joystick/Enclosure/LS4_Rear_Housing.stl
56.3 x 58.2 x 51.0

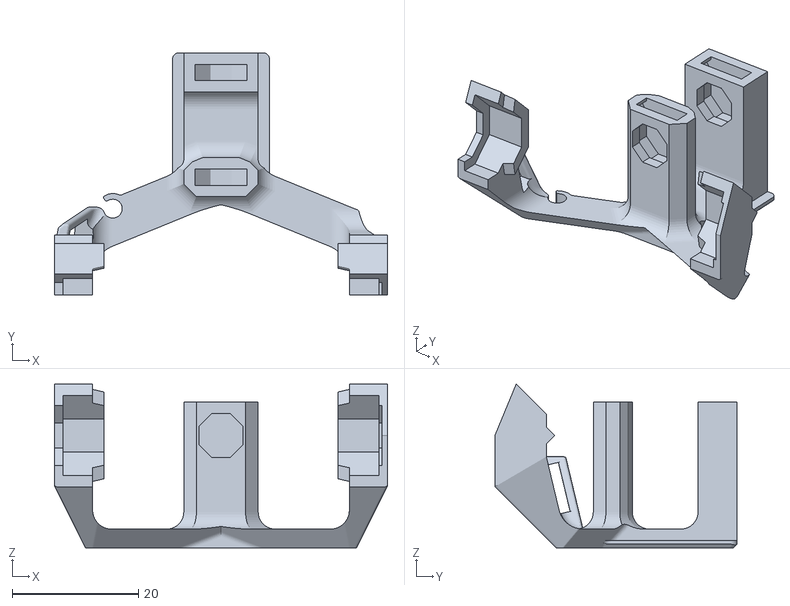
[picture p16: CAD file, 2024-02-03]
Build_Files/3D_Printing_Files/LS4_Joystick/Joystick/LS4_Gimbal_Sled.stl
52.8 x 38.4 x 26.0

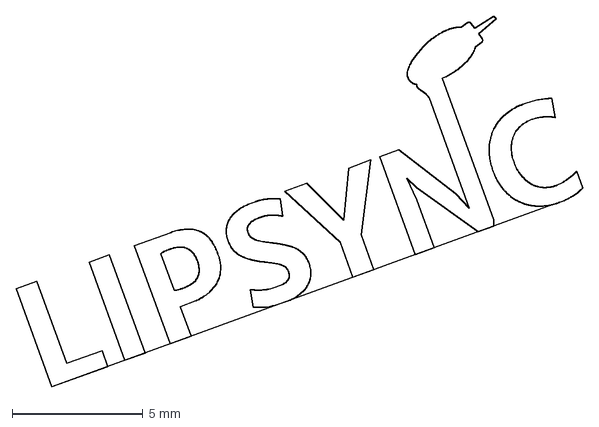
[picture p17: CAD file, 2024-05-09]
Design_Files/CAD_Design_Files/LipSync_Logo.dxf
21.7 x 14.2 mm

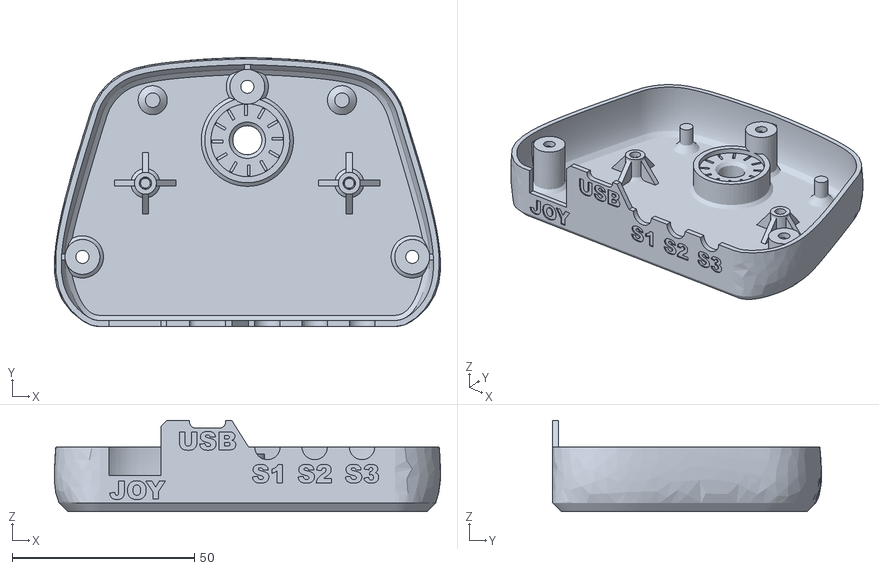
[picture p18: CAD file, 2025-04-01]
Build_Files/3D_Printing_Files/LS4_Hub/LS4_Hub_Bottom.stl
106.0 x 73.9 x 25.0

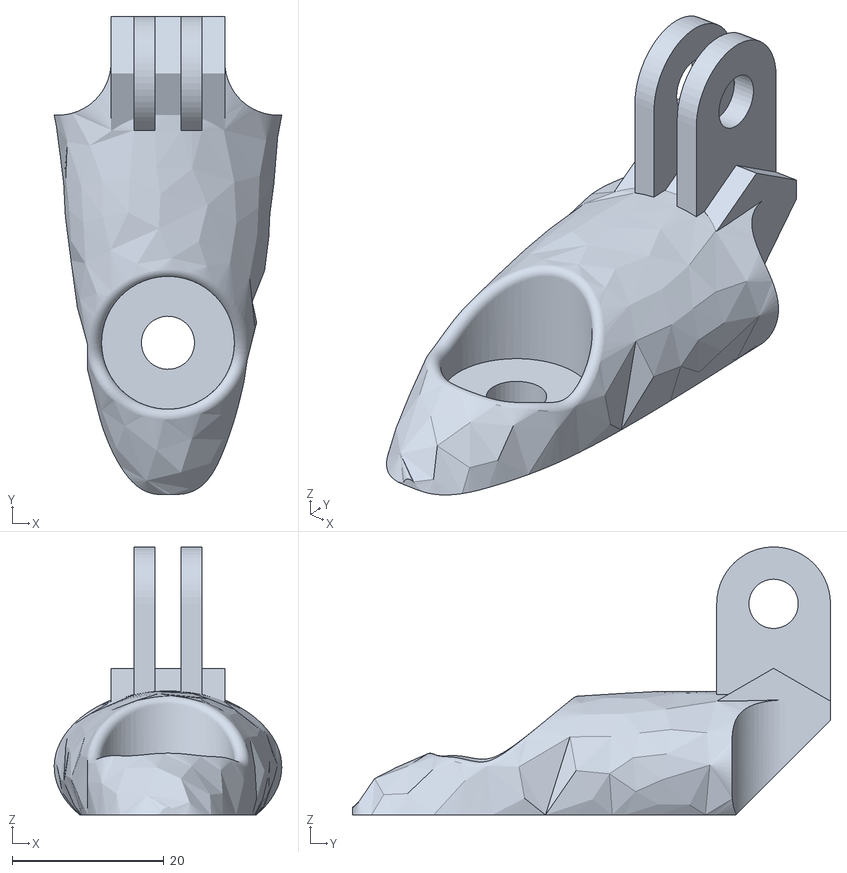
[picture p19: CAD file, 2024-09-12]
Build_Files/3D_Printing_Files/LS4_Hub/LS4_Hub_Stand/LipSync Hub Modular Mounting System/Build Files/StandAdaptorLowPoly.stl
30.0 x 63.0 x 35.3

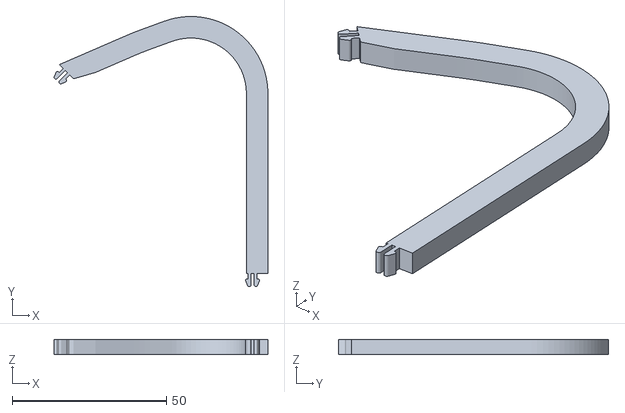
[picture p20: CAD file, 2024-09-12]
Build_Files/3D_Printing_Files/LS4_Hub/LS4_Hub_Stand/LS4_Hub_Stand_Leg.stl
69.4 x 87.6 x 5.00

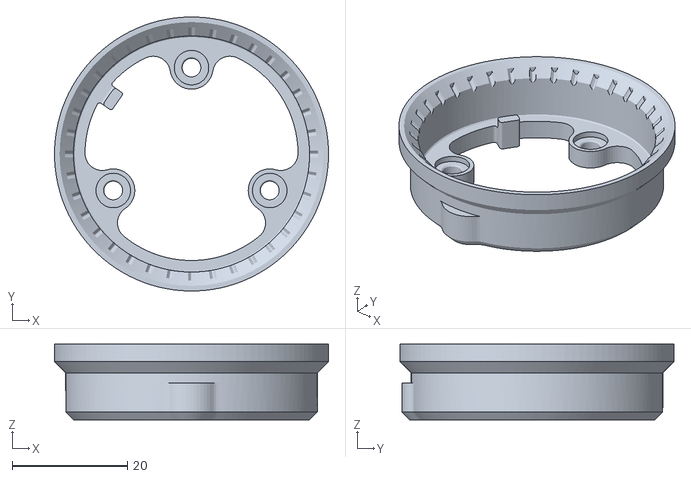
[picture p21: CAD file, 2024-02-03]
Build_Files/3D_Printing_Files/LS4_Joystick/Enclosure/LS4_Inner_Locking_Ring.stl
47.6 x 47.6 x 13.2

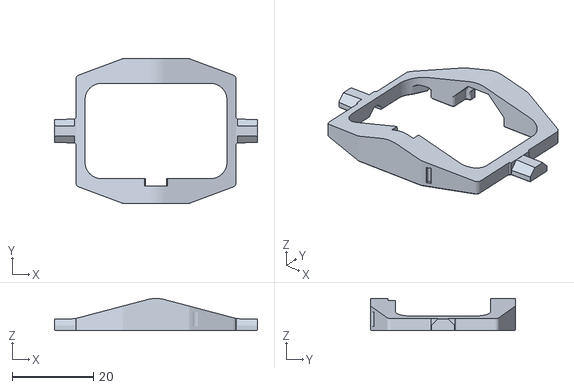
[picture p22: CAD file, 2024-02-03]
Build_Files/3D_Printing_Files/LS4_Joystick/Joystick/LS4_Outer_Gimbal_1.stl
50.1 x 35.7 x 7.95

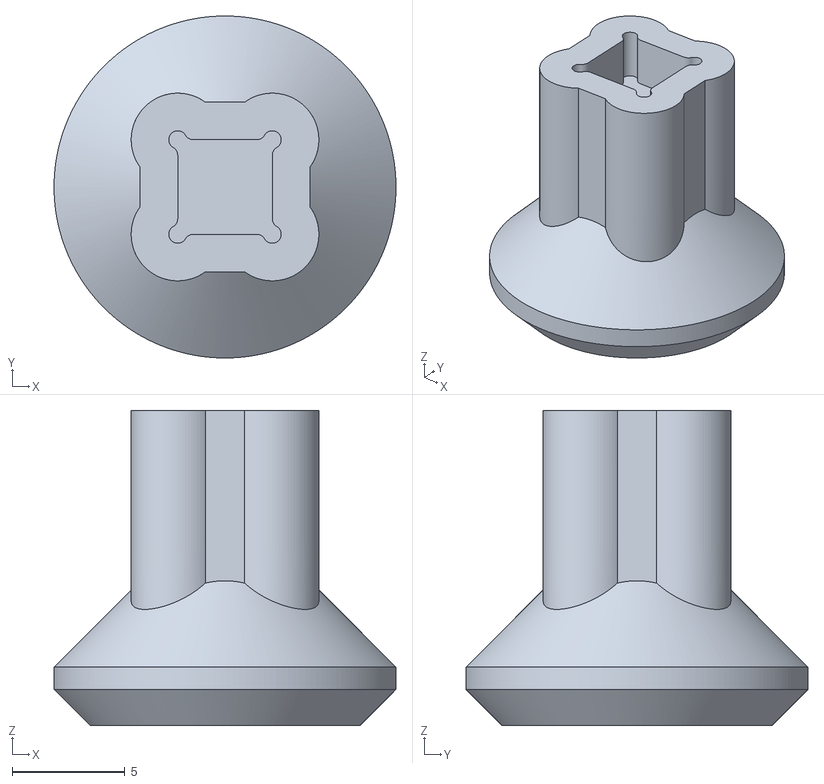
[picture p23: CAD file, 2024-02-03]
Build_Files/3D_Printing_Files/LS4_Hub/LS4_Hub_Next_Button.stl
15.2 x 15.2 x 14.0

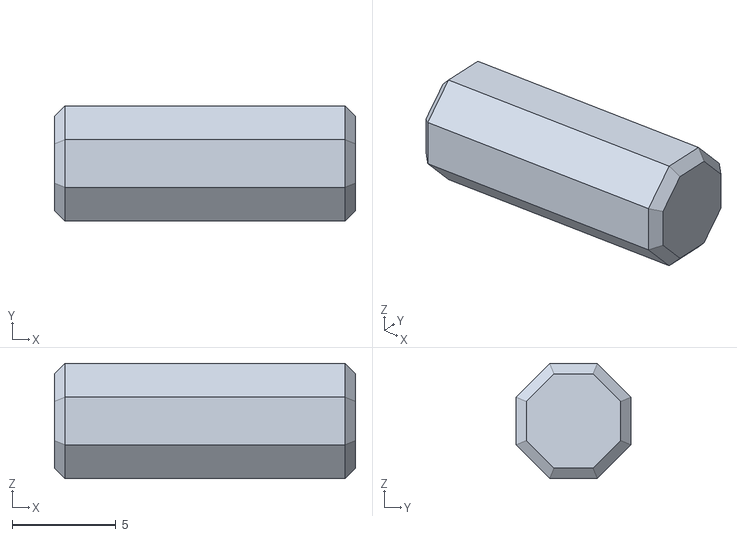
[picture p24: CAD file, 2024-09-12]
Build_Files/3D_Printing_Files/LS4_Hub/LS4_Hub_Stand/LipSync Hub Modular Mounting System/Build Files/Adaptor Pin.stl
14.5 x 5.54 x 5.54

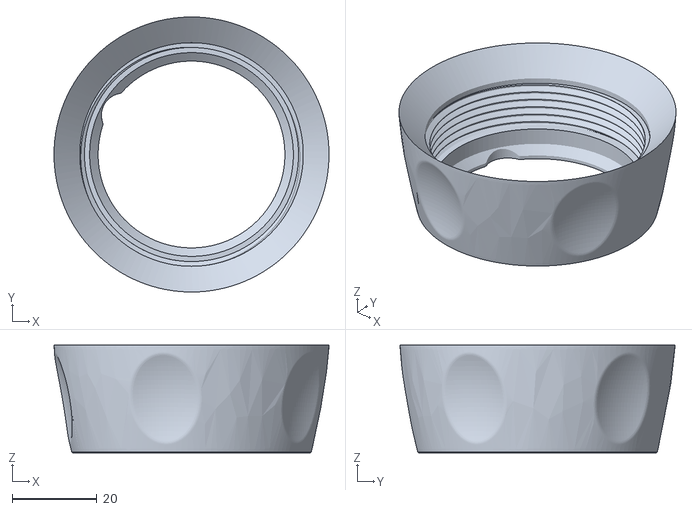
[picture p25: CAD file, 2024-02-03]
Build_Files/3D_Printing_Files/LS4_Joystick/Enclosure/LS4_Outer_Locking_Ring.stl
64.8 x 64.8 x 25.4

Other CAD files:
Build_Files/3D_Printing_Files/LS4_Joystick/Joystick/LS4_Gimbal_Shield.stl
Build_Files/3D_Printing_Files/LS4_Hub/LS4_Hub_LED_Spacer.stl
Build_Files/3D_Printing_Files/LS4_Hub/LS4_Hub_Stand/LipSync Hub Modular Mounting System/Build Files/StandArmLowPoly.stl
Build_Files/3D_Printing_Files/LS4_Joystick/Enclosure/LS4_Front_Cap.stl
Build_Files/3D_Printing_Files/LS4_Hub/LS4_Hub_Select_Button.stl
Build_Files/3D_Printing_Files/LS4_Hub/LS4_Hub_Stand/LipSync Hub Modular Mounting System/Build Files/PrintableBolt.stl
Build_Files/3D_Printing_Files/LS4_Hub/LS4_Hub_Stand/LipSync Hub Modular Mounting System/Build Files/PrintableBoltWithHandle.stl
Build_Files/3D_Printing_Files/LS4_Hub/LS4_Hub_Stand/LipSync Hub Modular Mounting System/Build Files/StandBaseLowPoly.stl
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

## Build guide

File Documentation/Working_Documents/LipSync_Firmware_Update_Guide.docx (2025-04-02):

# Overview

This document contains instructions on how to update the firmware on a LipSync.

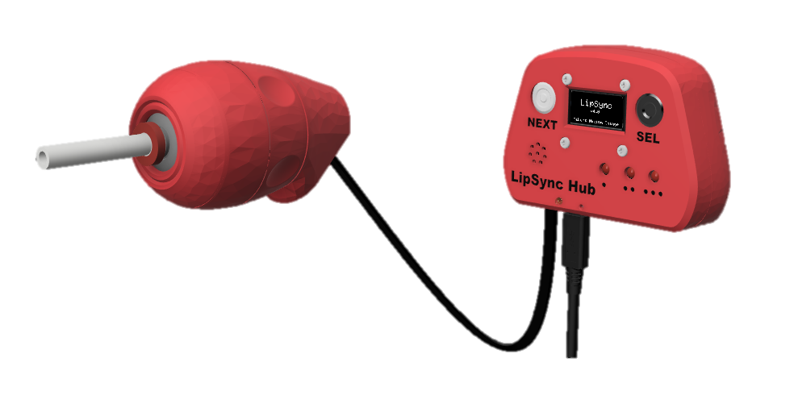
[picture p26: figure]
CAD render of final assembled LipSync Joystick and Hub

# Firmware Update Checklist

This list provides an overview of the steps required to build and deliver the device.

## To Do List

- Read through the Firmware Update Guide to become familiar with required components, tools, supplies, safety equipment, and overall steps.
- Confirm that the LipSync has V4 hardware.
- Download the latest firmware from the GitHub repository
- Set up the Arduino IDE on the computer
- Connect the LipSync to the Computer
- Note down the current settings
- Flash updated firmware to the LipSync
- Perform factory reset
- Restore settings

# Tool List

## Tools/ Equipment

Tool | Description | | Notes
T07 | Computer with Arduino IDE | Required | For flashing firmware to microcontroller

## Supplies

Supplies ID | Description | Quantity | Notes
n/a

# Firmware Update Guide

## Firmware Update

### Components

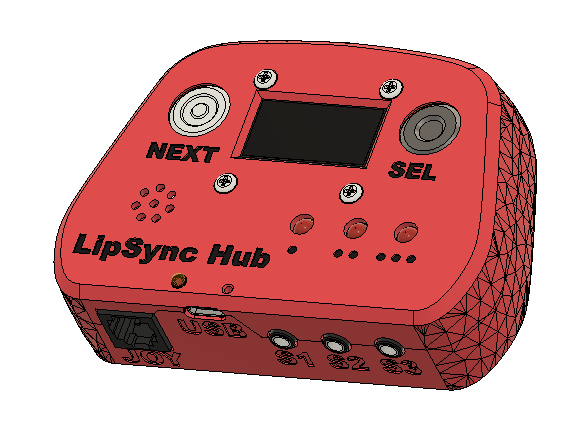
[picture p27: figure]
An assembled LipSync Hub
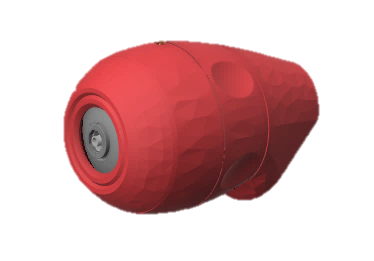
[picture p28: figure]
An assembled LipSync joystick without the mouthpiece
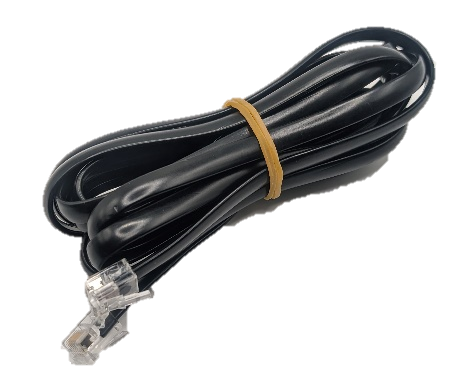
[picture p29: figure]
A black RJ11 cable

A1 | LipSync Hub | QTY 1 | A2 | LipSync Joystick | QTY 1 | A3 | LipSync Interface Cable (RJ11) | QTY 1

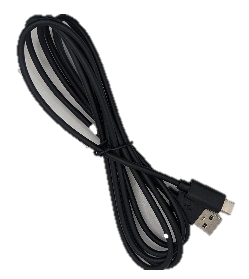
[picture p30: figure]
A black USB-C USB-A cable on a white background.
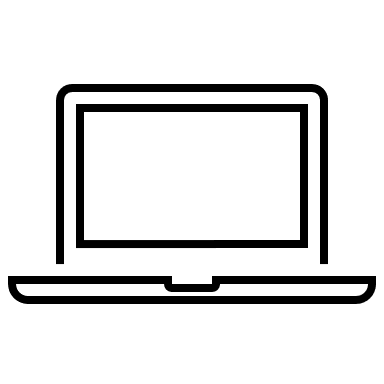
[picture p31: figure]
Laptop outline

A4 | USB-C-USB-A Cable | | A5 | Computer | QTY 1

### Tools

- Computer with Arduino IDE to flash firmware

### Part A: Firmware Flashing Preparation

#### Step A-01: Connect the LipSync Hub to the Computer using the USB Cable

Plug in the Hub (A1) to a computer using the USB Cable (A4).

#### Step A-02: Activate the Hub Menu

a) Activate the Hub Menu by briefly pressing, and then releasing both the Next and Select Buttons simultaneously. (Alternatively, press and hold the Select button for a very long press (> 3 second, or until Hub Light one turns on and then turns off again).

#### Step A-03: Note down the user’s settings

Setting | Value
Cursor Speed
Sound Mode
Light Brightness
Scroll Speed
Sip Threshold
Puff Threshold

### Part B: Arduino IDE Setup

This part sets up the computer to be able to flash the firmware. Some of these steps can be skipped if you already have the Arduino IDE installed or have previously worked with the same board.

#### Step B-01: Setup Arduino IDE on Computer

a) Download Arduino IDE for your operating system at https://www.arduino.cc/en/software
b) Install the Arduino IDE.

#### Step B-02: Open Arduino IDE

a) Open Arduino IDE.

#### Step B-03: Setup Arduino IDE for Seeed Studio Xiao nRF52840 Development Board

a) Click on File -> Preferences.
b) Locate the text field that says Additional Boards Manager URLs beside it.
c) Copy and paste the following link into the field as a new line:
  a. https://files.seeedstudio.com/arduino/package_seeeduino_boards_index.json
d) Click on OK.

#### Step B-04: Restart Arduino IDE

a) Close and reopen the Arduino IDE.

#### Step B-05: Install the Board Drivers

a) Open the Boards Manager option from the Tools-> Board-> Boards Manager...,
b) Search for “Seeed nrf52” and select “Seeed nRF52 Boards” by Seeed Studio.
c) Click Install to install the board.

#### Step B-06: Install Libraries

a) In the Arduino IDE, go to Tools -> Manage Libraries…
b) For each of the libraries in the table below, search for the name, and click Install.
c) If prompted to install any dependent libraries, click OK.

Name | Author
Adafruit_LPS2X | Adafruit
Adafruit_LPS35HW | Adafruit
Adafruit_SSD1306 | Adafruit
ArduinoJson | Benoit Blanchon
TLV493D-A1B6 | Infineon Technologies
Adafruit_TinyUSB | Adafruit

#### Step B-07: Download the latest firmware

Download the Firmware_Files from the GitHub Repository: https://github.com/makersmakingchange/LipSync/blob/main/Build_Files/Firmware_Files/LipSync_Firmware.zip

#### Step B-08: Extract the firmware

Extract / unzip the folder to a known location. Confirm that you have the following folder structure:

- LipSync_Firmware (folder)
- LipSync_Firmware.ino
- LSAPI.ino
- LSTest.ino
- LSBLE.h
- LSBuzzer.h
- LSCircularBuffer.h
- LSConfig.h
- LSInput.h
- LSJoystick.h
- LSMemory.h
- LSOutput.h
- LSPressure.h
- LSScreen.h
- LSTimer.h
- LSUSB.h
- LSUtils.h
- LSWatchdog.h

#### Step B-09: Open LipSync_Firmware.ino in Arduino IDE

Open LipSync_Firmware.ino with Arduino IDE. The files listed above should appear as tabs.

#### Step B-10: Set the target Board

Select Seeed Xiao NRF52840 from Tools -> Board -> Seeed NRF52 Boards

#### Step B-11: Select the Port

Select the correct port from Tools -> Port menu.

#### Step B-12: Compile and Verify the Code

Verify the code.

#### Step B-13: Connect the LipSync Hub to the computer

Connect the LipSync Hub using the USB cable to the computer.

#### Step B-14: Confirm that the firmware uploaded correctly.

Check the Output panel of the Arduino IDE to confirm that the firmware has been uploaded correctly. The output should say ‘Device programmed’.

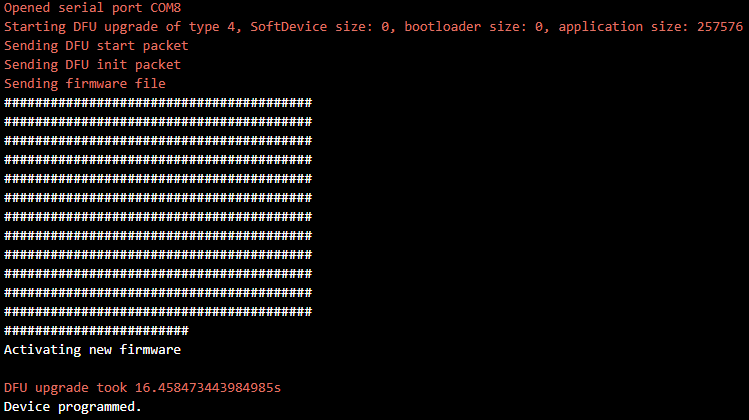
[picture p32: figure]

#### Step B-15: Disconnect and reconnect the USB cable from the Hub

Disconnect the USB cable from the Hub. Wait 15 seconds, and then reconnect the power.

#### Step B-16: Perform a factory reset.

Activate the Hub Menu by short simultaneous press then release on both Hub buttons. Navigate down to the More Menu, then navigate down to the Factory Reset.

#### Step B-17: Restore any user settings

Disconnect the USB cable from the Hub. Wait 15 seconds, and then reconnect the power.

### Part C: Verify Operation

#### Step C-01: Verify the PCB and Sensors work as expected.

When the USB cable is connected, a green LED should illuminate on each of the sensors and the back of the display.

Once the code is uploaded, confirm that:

- The LipSync plays the startup noise
- The 3 LEDs on the Hub turn on briefly
- The multicoloured mode LED turns on
- The display should shows the splash screen
- There are no error messages on the display

If all goes well, proceed to the next step. If there are any problems, unplug the USB cable and proceed to troubleshooting.

#### Step C-02: Verify functionality with Joystick

Ensure that the joystick is in USB mouse mode and confirm the following:

- Does mouse move when you move joystick?
- Does mouse stop moving when you release the joystick (i.e., no drift)?
- Can you perform left and right clicks with Next and Sel buttons?
- Plug in assistive switches - can you perform left, right, and middle clicks with assistive switches?

# Troubleshooting

1. My Arduino IDE is stuck when uploading code to the board.

You can first try to reset the board by clicking the "Reset Button" once. If that does not work, rapidly click it twice to enter bootloader mode. If that also doesn't work, disconnect the board from the PC, and connect the board again.

2. My board is not showing up as a serial device on Arduino IDE.

You can first try to reset the board by clicking the "Reset Button" once. If that does not work, rapidly click it twice to enter bootloader mode.

If neither of those options work, make sure your USB-C cable is securely connected on both ends, and that it is a data transfer cable, not a power only cable.

3. The LipSync plays an error tone and then lists an error in Safe Mode.

First, unplug the LipSync Hub from power for 15 seconds, and then plug it back into the host device or power. If the error persists, refer to the User Guide to resolve the error.

© 2024-2025 Neil Squire Society. This work is licensed under the CC BY SA 4.0 License: http://creativecommons.org/licenses/by-sa/4.0 Files available at https://github.com/makersmakingchange/LipSync Page 1 of 1

V4.1 | MARCH 2025 LipSync firmware Update Guide

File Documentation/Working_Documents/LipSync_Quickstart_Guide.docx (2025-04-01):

LipSync User Guide PDF QR Code

User Guide (https://github.com/makersmakingchange/LipSync/blob/main/Documentation/LipSync_User_Guide.pdf)

# Introduction

The LipSync is a mouth-operated sip-and-puff joystick that allows a user with limited or no arm mobility to control a computer, gaming console, smart phone, or tablet. This Quickstart Guide is meant to briefly introduce the functions and use of the LipSync. For more detailed information, please consult the User Guide.

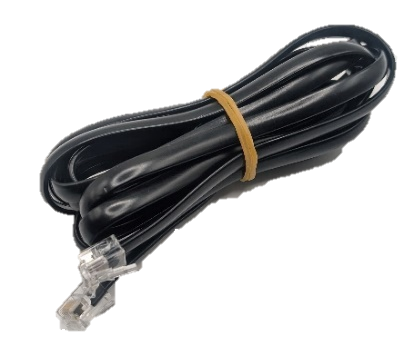
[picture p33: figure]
A picture of the RJ11 cable
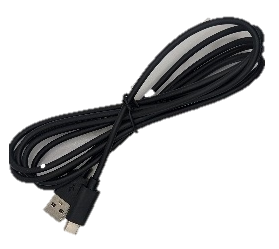
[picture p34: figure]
A photo of a black USB-C cable on a white background.

# Features

LipSync Interface Cable

USB-C to USB-A Cable

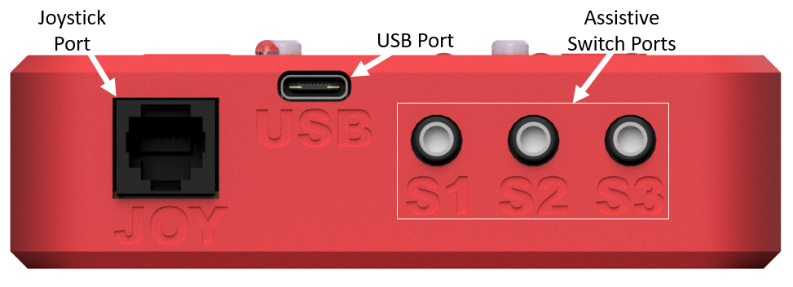
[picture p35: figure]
The bottom of the LipSync Hub. From left to right, the Joystick Port, USB Port, and Assistive Switch ports S1, S2, and S3.
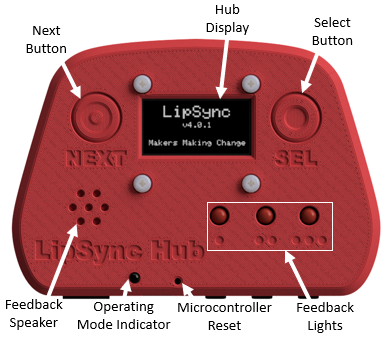
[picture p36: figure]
A CAD render of the front of the LipSync hub with the features all labeled
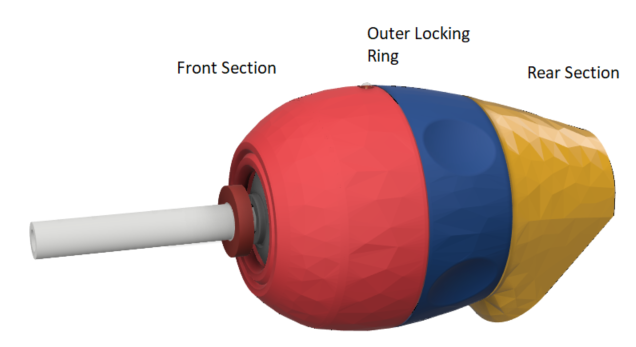
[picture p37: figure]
A CAD render of the LipSync joystick with the front section, locking ring, and rear section labeled
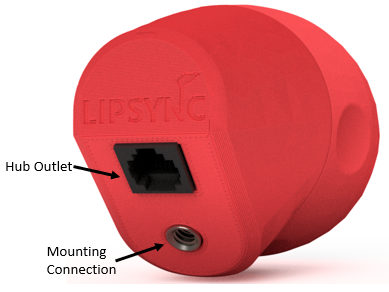
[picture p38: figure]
A CAD render of the LipSync joystick with the hub outlet and mounting connection port labeled

Filtered Mouthpiece

Power and Orientation LED

# Setting up the LipSync

The following are the general steps needed to setup your LipSync device:

2. Mount LipSync Joystick
3. Mount LipSync Hub
4. Connect LipSync Interface Cable
5. Optional: Connect up to 3 Assistive Switches
6. Connect the LipSync Hub to the Host Device
7. Once powered, wait until device initializes before moving joystick.

## Connecting the LipSync to the Host Device

### USB Connections

For direct USB connection to the host device, connect the appropriate USB cable from the LipSync Hub into the host device. Use an adapter if necessary.

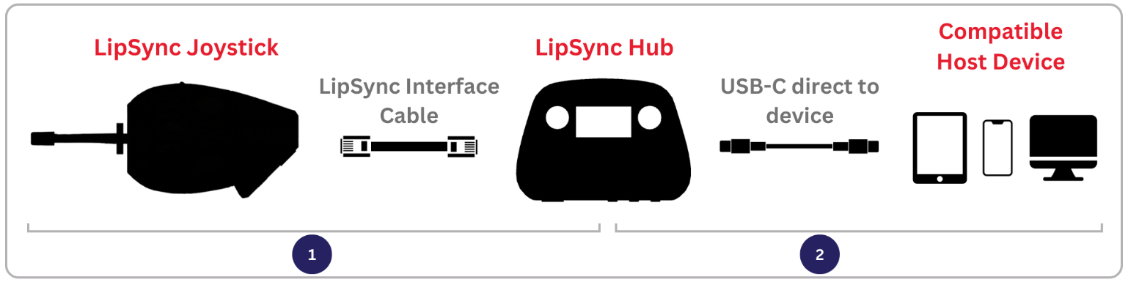
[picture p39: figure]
A diagram showing how to set up the LipSync to connect to an Android device. The Joystick is connected to the Hub via the interface cable, and the hub is connected to the device via a USB C cable.

For connection to the host device with an external power source, plug a power splitting adapter into the host device and connect the LipSync Hub and external power source to the splitter. Use an Adapter if necessary. Required for iOS USB connection.

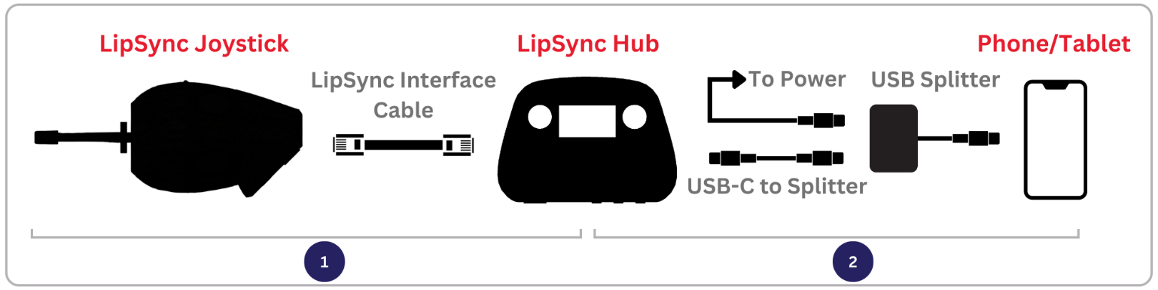
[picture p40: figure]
A diagram showing how to set up the LipSync to connect to an Android device using an external power source. The Joystick is connected to the Hub via the interface cable, and the hub is connected to a USB splitter via a USB C cable. An external power source is attached to the USB splitter, and the 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

### Wireless Connections

For wireless connection to the host device, plug the LipSync Hub directly into any power source using the appropriate adapter as required. Change the operating mode to BT Mouse through the Hub Menu
Find “LS_(DeviceID)” in the host device Bluetooth menu to pair and connect.

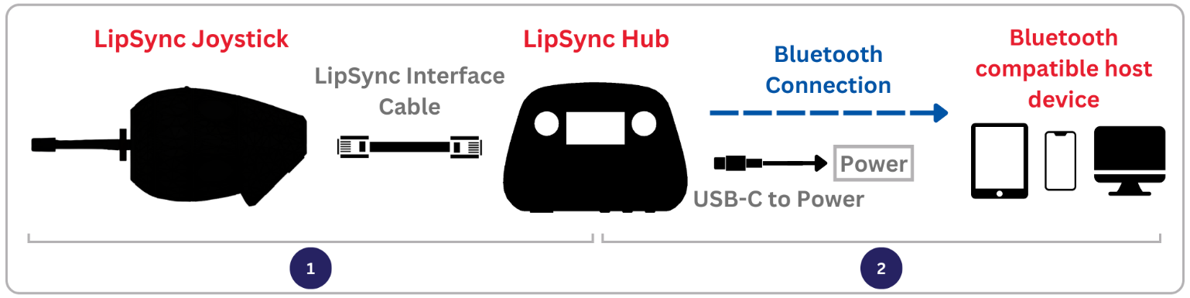
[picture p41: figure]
A diagram showing how to set up the LipSync to connect to a Bluetooth device using an external power source. The Joystick is connected to the Hub via the interface cable, and the hub is connected to an external power source. The Hub is connected to the host device via Bluetooth

Cursor Setup on iOS Devices

Open your device’s Settings > Accessibility > Touch > AssistiveTouch > Turn it on.

## Input Actions

Input | | | Input Duration | Output (based on Operating Mode)
Sip and Puff | Assistive Switches | Hub Buttons | | Mouse | Gamepad | Hub Menu
Puff | S1 | Select | < 1 sec | Left click | Button 1 | Select
| | | 1-3 sec | Start Drag Mode | Button 3 | -
| | | > 3 sec | Enter Hub Menu | Enter Hub Menu | Exit Hub Menu
- | S2 | - | < 1 sec | Middle Click | Button 5 | -
| | | 1-3 sec | N/A | Button 6 | -
| | | > 3 sec | Perform Center Reset | Perform Center Reset | -
Sip | S3 | Next | < 1 sec | Right click | Button 2 | Next
| | | 1-3 sec | Start Scroll Mode | Button 4 | -
| | | > 3 sec | Middle Click | Button 5 | -
- | S1 + S3 | Next + Select | < 1 sec | Enter Hub Menu | Enter Hub Menu | Exit Hub Menu
Joystick | | | - | Cursor movement | Joystick movement

## Hub Menu Settings

The Menu on the Hub Display provides a way to changing operating modes, adjusting settings, activate calibrations, and reset the LipSync device. See the Input Action table for how to access and navigate the menu. See the User Guide for more details.

## Troubleshooting

### Cursor Issues

If you are experiencing cursor drift, perform a center reset in one of the following ways:

Option A: Trigger Center Reset Either by: - Activate the Hub Menu and navigate to Center Reset - Using a very long press of assistive switch 2 | Option B: Turn it off and then on again. Do not touch the joystick until “Ready to use” is displayed on the Hub Display. - Disconnect/Reconnect the USB cable from the LipSync Hub. - Restart the device through the Hub Menu..

### Error Messages

If a hardware error is detected on startup, the LipSync will enter Safe Mode and display an error code. Refer to the User Guide for how to resolve the error. If issues persist, contact Support.

## Support

For support, contact the maker of your device or Makers Making Change at info@makersmakingchange.com

© 2024-2025 by Neil Squire. This work is licensed under the CC BY SA 4.0 License: http://creativecommons.org/licenses/by-sa/4.0 Files available at https://github.com/makersmakingchange/LipSync Page 2 of 3

V4.1 | MARCH 2025 LipSync Quickstart Guide

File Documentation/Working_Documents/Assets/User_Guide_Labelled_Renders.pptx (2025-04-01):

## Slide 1

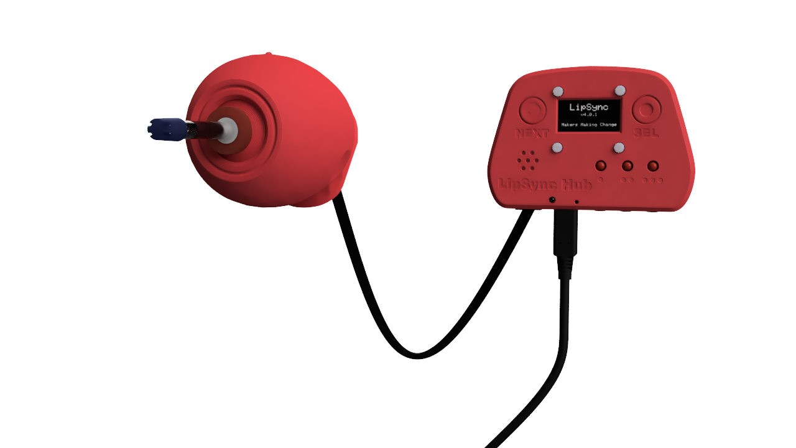
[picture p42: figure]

LipSync Joystick

LipSync Hub

LipSync Interface Cable

USB Cable

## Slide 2

Next Button

Hub Display

Select Button

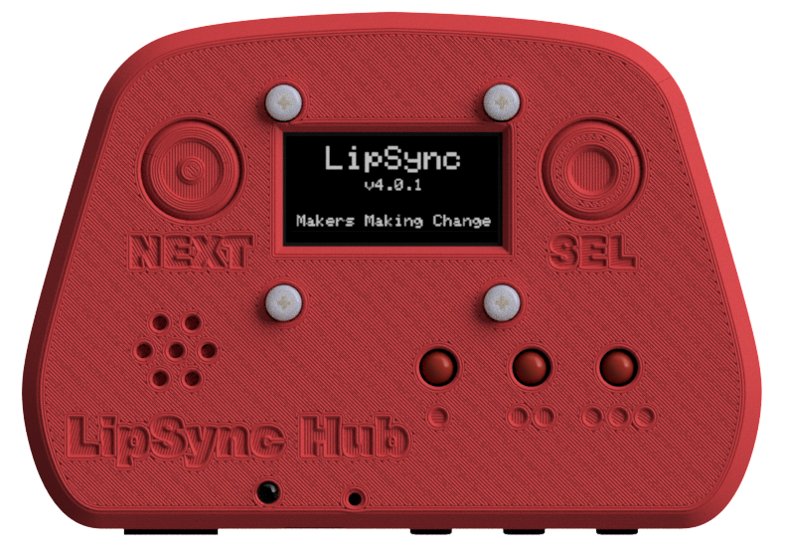
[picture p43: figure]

Feedback Speaker

Operating Mode Indicator

Microcontroller Reset

Feedback Lights

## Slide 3

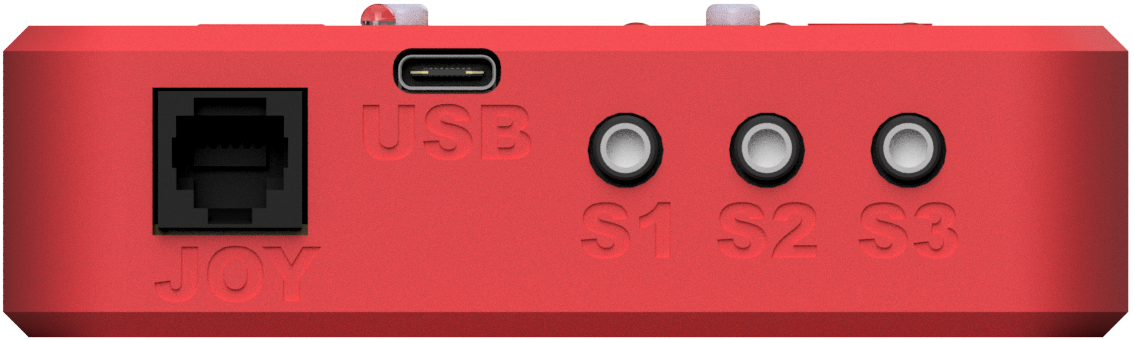
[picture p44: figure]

Joystick Port

USB Port

Assistive Switch Ports

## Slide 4

Joystick Port

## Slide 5

Assistive Switch Ports

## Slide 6

Mounting Connection

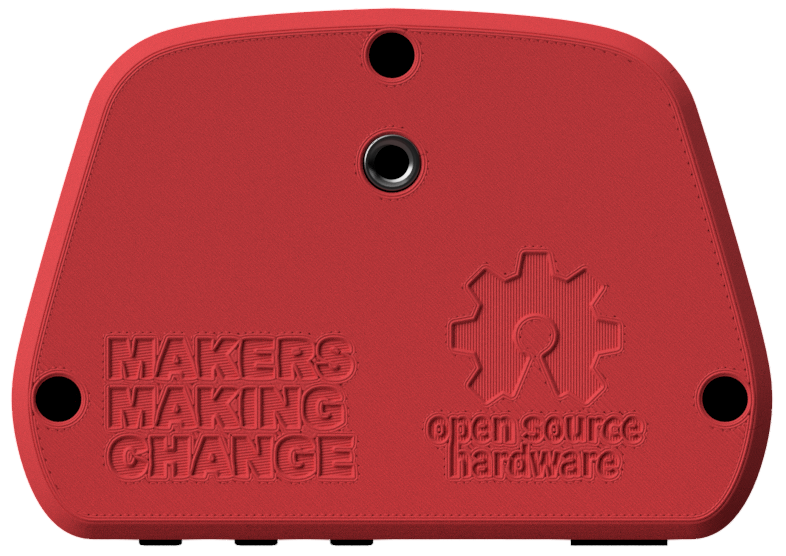
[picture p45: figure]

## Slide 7

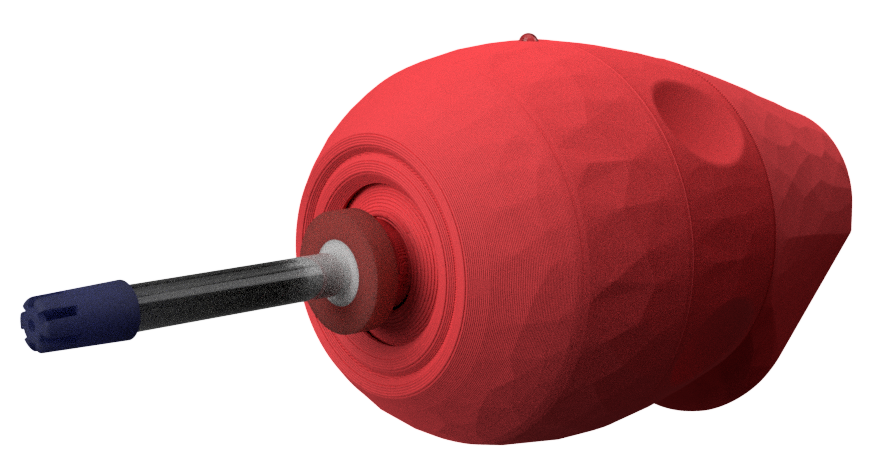
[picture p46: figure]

Power and Orientation LED

Filtered Mouthpiece

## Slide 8

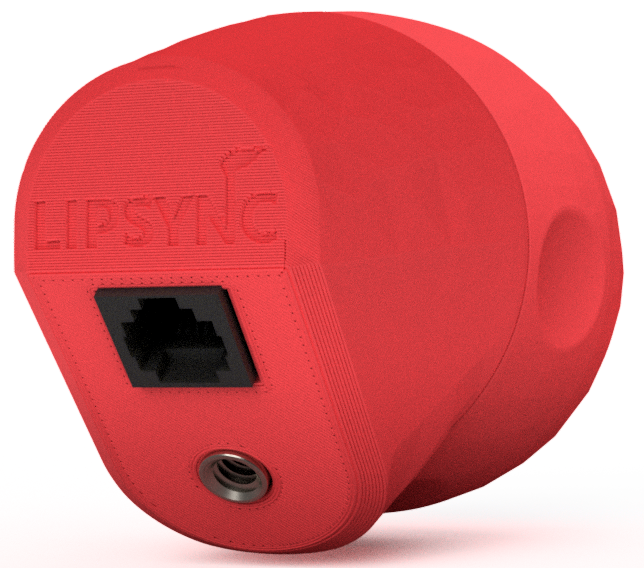
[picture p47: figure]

Hub Port

Mounting Connection

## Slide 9

Hub Port

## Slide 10

Outer Locking Ring

Front Section

Rear Section

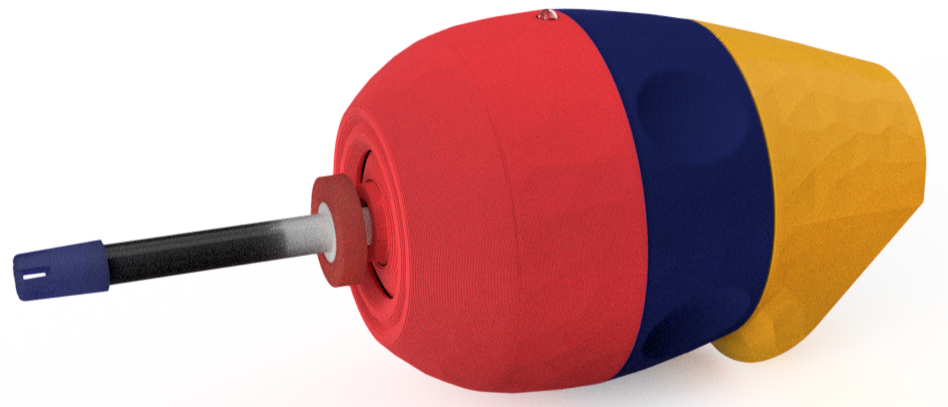
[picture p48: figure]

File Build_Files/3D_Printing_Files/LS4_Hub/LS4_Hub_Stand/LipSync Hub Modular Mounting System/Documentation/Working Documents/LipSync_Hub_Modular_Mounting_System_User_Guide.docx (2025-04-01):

## Introduction

The LipSync Hub Modular Mounting System is a stand for the LipSync Hub that allows the height and angle of the Hub to be set independently of each other. The base version has a base, an arm, and a hub adaptor, but it is possible to add multiple arms, or different bases to suit different needs. It is a derivative of the Modular Mounting System (https://www.thingiverse.com/thing:2194278) on Thingiverse.

## Features

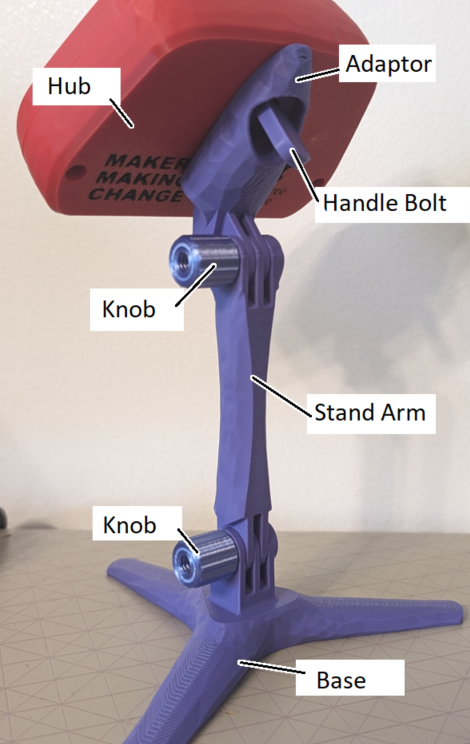
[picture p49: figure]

## Usage

To adjust the angle and height of the stand, loosen the knobs or nuts on the joints of the stand. The stand can then be posed to the desired position, and the knobs tightened to lock the joints in place.

## Compatibility

Hardware: The system is designed for use with commercial ¼-20 hardware, but it will also work with 3D printed ¼-20 hardware, as well as commercial M5 and M6 hardware.

Parts: The LipSync Hub Modular Mounting System is a derivative of the Modular Mounting System (https://www.thingiverse.com/thing:2194278) by HeyVye on thingiverse.com. The LipSync Hub Modular mounting system is backwards compatible with the original, but only when using M5 hardware, as that is the only hardware that works with the original system.

## Specifications

Base Diameter: 15 cm

Maximum Height: 20 cm

Weight: 41 g

## Cleaning

The Modular Mounting System can be wiped clean with a damp cloth.

© 2024 by Neil Squire Society/Makers Making Change. This work is licensed under the CC BY SA 4.0 License: http://creativecommons.org/licenses/by-sa/4.0 Files available at <MMC Project Library Link> Page 2 of 3

V4.1 | April 2024 LipSync Hub Modular Mounting System user Quick Guide

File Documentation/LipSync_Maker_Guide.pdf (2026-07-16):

V4.1.1 | MARCH 2025

## LipSync

## MAKER GUIDE

© 2024-2025 Neil Squire Society. This work is licensed under the CC BY SA 4.0 License: http://creativecommons.org/licenses/by-sa/4.0
Files available at https://github.com/makersmakingchange/LipSync | Page 1 of 83

### Overview

This document contains the necessary information to build the LipSync. The Maker Checklist outlines the required steps, including questions for the User. The Tool List contains a comprehensive list of all tools and supplies required to complete the build. The Custom PCB contains information on how to order the required printed circuit board (PCB). The 3D Printing Guide contains print settings and quantities for the 3D printed components. The Assembly Guide contains all the necessary steps to assemble and program the device. Finally, the Testing Guide contains a set of tests to confirm the LipSync is working properly.

## MAKER GUIDE

Files available at https://github.com/makersmakingchange/LipSync | Page 2 of 83

### Contents

Overview | 1
Maker Checklist | 5
Maker To Do List | 5
Items to Give to User | 5
Tool List | 6
Tools/ Equipment | 6
Supplies | 6
Custom PCB Guide | 7
Ordering the Custom PCB | 7
3D Printing Guide | 8
3D Printing Summary | 8
3D Printing Settings | 8
Customization Options | 9
Joystick | 9
Hub | 9
Post-Processing | 10
Examples of Quality Prints | 10
Master Component List | 12
Assembly Guide | 21
Part A: Hub PCB Assembly | 23
Part A: Components | 23
Part A: Tools | 24
Part A: Personal Protective Equipment (PPE) | 24
Part A: Hub PCB Assembly Steps | 25
Part B: Joystick Component Preparation | 32
Part B: Components | 32
Part B: Tools | 32
Part B: Personal Protective Equipment (PPE) | 32
Part B: Assembling Hub Enclosure Steps | 33
Part C: Flashing Firmware | 37

## MAKER GUIDE

Files available at https://github.com/makersmakingchange/LipSync | Page 3 of 83
Part C: Components | 37
Part C: Tools | 37
Part C: Firmware Flashing Steps | 38
Part D: Hub Enclosure Assembly | 42
Part D: Components | 42
Part D: Tools | 43
Part D: Personal Protective Equipment (PPE) | 43
Part D: Assembling Hub Enclosure Steps | 44
Part E: Joystick Gimbal Assembly | 49
Part E: Components | 49
Part E: Tools | 50
Part E: Personal Protective Equipment (PPE) | 50
Part E: Joystick Gimbal Assembly Steps | 51
Part F: Joystick Housing Assembly | 63
Part F: Components | 63
Part F: Tools | 64
Part F: Personal Protective Equipment (PPE) | 64
Part F: Assembling Joystick Housing Steps | 65
Part G: Mouthpiece Assembly | 74
Part G: Components | 74
Part G: Tools | 74
Part G: Personal Protective Equipment (PPE) | 74
Part G: Assembling the Mouthpiece Steps | 75
Part H: Initial LipSync Setup and Testing | 78
Part H: Components | 78
Part H: Initial LipSync Setup Steps | 78
Testing Guide | 80
Testing the LipSync | 80
Testing Mouse Mode | 80
Testing Sip and Puff | 80
Testing External Switches | 81

## MAKER GUIDE

Files available at https://github.com/makersmakingchange/LipSync | Page 4 of 83
Testing Hub Buttons | 81
Troubleshooting | 82

## MAKER GUIDE

Files available at https://github.com/makersmakingchange/LipSync | Page 5 of 83

### Maker Checklist

This list provides an overview of the steps required to build and deliver the device.

### Maker To Do List

Read through the Maker Guide to become familiar with required components, tools, supplies, safety equipment, and overall assembly steps.
Talk to User about customization options (e.g., color, any special requests, etc.)
- Hub Color
- Joystick Color
- Hub Stand
Order Custom PCBs.
Order hardware components.
Print 3D printed components.
Gather tools, supplies, and safety equipment. Assemble the LipSync Hub.
Assemble the LipSync Joystick.
Assemble the LipSync Mouthpieces. Assemble and flash firmware to the LipSync. If requested, print and assemble the Hub Stand. Test the LipSync.
Print LipSync Info Sheet.

### Items to Give to User

(1) LipSync Joystick. Assembled and tested.
(1) LipSync Hub. Assembled, flashed, and tested.
(1) LipSync Interface Cable.
(1) USB-C Cable.
(5) Mouthpiece Assemblies, sealed in a clean baggy. Printed Info Sheet

## MAKER GUIDE

Files available at https://github.com/makersmakingchange/LipSync | Page 6 of 83

### Tool List

Tools/ Equipment
Tool | Description | Notes
T01 | Soldering Iron | Required | For soldering electronic components.
T02 | Flush cutters | Required | For trimming soldered leads
T03 | Needle Nose Pliers | Recommended | Installing bearings; routing cables.
T04 | Crescent wrench / wrench / hex key | Recommended | For installing tee nuts into Hub and Joystick enclosures.
T05 | Screwdriver, Phillips, Small | Required | A jeweller’s screwdriver or similar for securing M2.5 machine screws.
T06 | Sandpaper / Files | Recommended | Cleaning up 3d prints; fixing bearing fits
T07 | Computer with Arduino IDE | Required | For flashing firmware to microcontroller

Supplies
Supplies ID | Description | Quantity | Notes
S01 | Solder

## MAKER GUIDE

Files available at https://github.com/makersmakingchange/LipSync | Page 7 of 83

### Custom PCB Guide

The LipSync V4.0 uses one (1) custom circuit board for the Hub.

The Custom PCB can be ordered from one of a variety of PCB Manufacturers. Typically, the minimum quantity for a custom PCB is five. Shipping options vary significantly in cost and shipping time. Plan on at least a week from the time of order to the PCBs arrival.

### Ordering the Custom PCB

1. Select a PCB Fabrication Company
a. JLPCB (https://jlcpcb.com/)
b. PCBWay (https://www.pcbway.com/)
c. OSH Park (https://oshpark.com/)
d. Seeed Fusion PCB (https://www.seeedstudio.com/fusion_pcb.html)
2. Create an account or use a guest login.
3. Upload the Gerber Files (e.g., LipSync_Hub_PCB_YYY-MM-DD.zip).
4. Select the fabrication options:
a. PCB Layers: 2 Layers
b. PCB Quantity: 5
c. PCB Thickness: 1.5 mm
d. Surface Finish: HASL
e. PCB Color: Choose what you like. Note that certain colors may impact build time.
f. The default settings for the other settings should work.
5. Select shipping option.
a. Shipping options and costs vary significantly. Select the best option based on your budget and timing.
6. Submit the order.

## MAKER GUIDE

### 3D Printing Guide

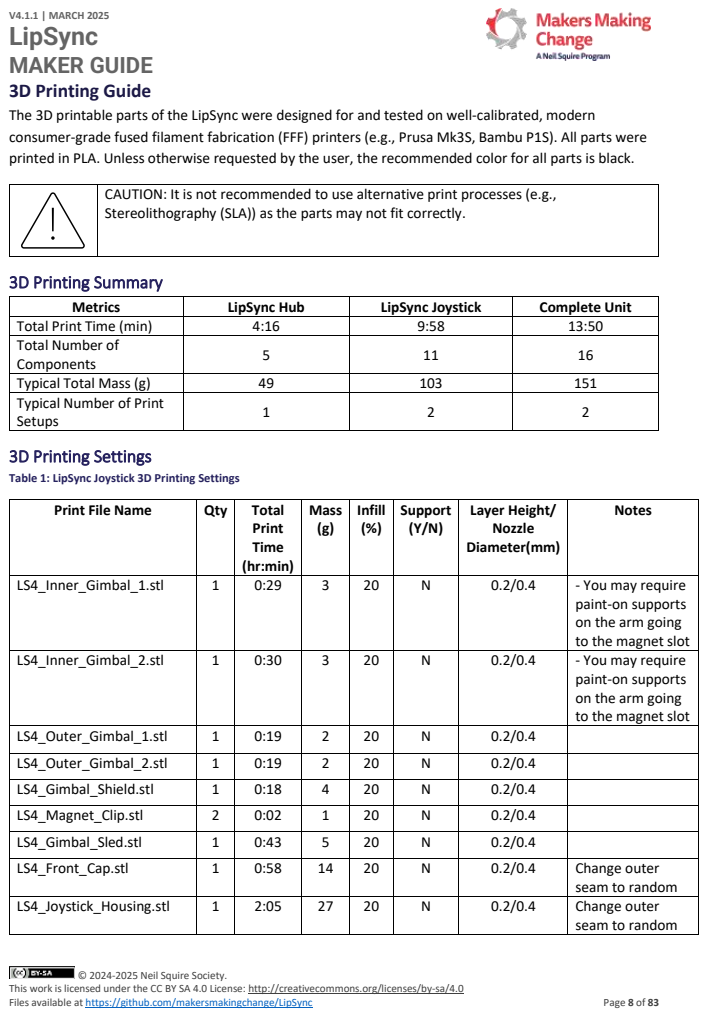
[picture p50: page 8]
Files available at https://github.com/makersmakingchange/LipSync; Page 8 of 83; 3D Printing Summary; 3D Printing Settings

The 3D printable parts of the LipSync were designed for and tested on well-calibrated, modern
consumer-grade fused filament fabrication (FFF) printers (e.g., Prusa Mk3S, Bambu P1S). All parts were
printed in PLA. Unless otherwise requested by the user, the recommended color for all parts is black.

CAUTION: It is not recommended to use alternative print processes (e.g.,
Stereolithography (SLA)) as the parts may not fit correctly.

Metrics | LipSync Hub | LipSync Joystick | Complete Unit

Total Print Time (min) | 4:16 | 9:58 | 13:50
Total Number of Components | 5 | 11 | 16

Typical Total Mass (g) | 49 | 103 | 151
Typical Number of Print Setups | 1 | 2 | 2

Table 1: LipSync Joystick 3D Printing Settings

Print File Name | Qty | Total Print Time (hr:min) | Mass (g) | Infill (%) | Support (Y/N) | Layer Height/ Nozzle Diameter(mm) | Notes

LS4_Inner_Gimbal_1.stl | 1 | 0:29 | 3 | 20 | N | 0.2/0.4 | - You may require paint-on supports on the arm going to the magnet slot

LS4_Inner_Gimbal_2.stl | 1 | 0:30 | 3 | 20 | N | 0.2/0.4 | - You may require paint-on supports on the arm going to the magnet slot

LS4_Outer_Gimbal_1.stl | 1 | 0:19 | 2 | 20 | N | 0.2/0.4
LS4_Outer_Gimbal_2.stl | 1 | 0:19 | 2 | 20 | N | 0.2/0.4
LS4_Gimbal_Shield.stl | 1 | 0:18 | 4 | 20 | N | 0.2/0.4
LS4_Magnet_Clip.stl | 2 | 0:02 | 1 | 20 | N | 0.2/0.4
LS4_Gimbal_Sled.stl | 1 | 0:43 | 5 | 20 | N | 0.2/0.4
LS4_Front_Cap.stl | 1 | 0:58 | 14 | 20 | N | 0.2/0.4 | Change outer seam to random

LS4_Joystick_Housing.stl | 1 | 2:05 | 27 | 20 | N | 0.2/0.4 | Change outer seam to random

## MAKER GUIDE

Files available at https://github.com/makersmakingchange/LipSync | Page 9 of 83
Print File Name | Qty | Total Print Time (hr:min) | Mass (g) | Infill (%) | Support (Y/N) | Layer Height/ Nozzle Diameter(mm) | Notes
LS4_Outer_Locking_Ring.stl | 1 | 1:15 | 17 | 20 | N | 0.2/0.4 | Change outer seam to random
LS4_Inner_Locking_Ring.stl | 1 | 0:33 | 6 | 20 | N | 0.2/0.4
LS4_Rear_Housing.stl | 1 | 2:27 | 22 | 20 | N | 0.2/0.4 | Change outer seam to random

Table 2: LipSync Hub 3D Printing Settings

Print File Name | Qty | Total Print Time (hr:min) | Mass (g) | Infill (%) | Support(Y/N) | Layer Height/ Nozzle Diameter(mm) | Notes
LS4_Hub_Top | 1 | 1:34 | 20 | 15 | N | 0.2/0.4
LS4_Hub_Bottom | 1 | 2:07 | 26 | 15 | N | 0.2/0.4
LS4_Hub_LED_Spacer | 1 | 0:13 | 2 | 15 | N | 0.2/0.4
LS4_Hub_Next_Button_Pusher | 1 | 0:11 | 1 | 15 | N | 0.2/0.4
LS4_Hub_SEL_Button_Pusher | 1 | 0:11 | 1 | 15 | N | 0.2/0.4

### Customization Options

Joystick
Each outward facing component of the Joystick enclosure (Front Cap, Joystick Housing, Outer Locking Ring, and Rear Housing) can be printed in a combination of different or matching colors to customize the look of the LipSync Joystick. Otherwise, muted or neutral tones (e.g., black or grey) are generally preferred.

Hub
There are several options for customizing the look of the LipSync Hub depending on the color(s) of the filament available.

## MAKER GUIDE

Files available at https://github.com/makersmakingchange/LipSync | Page 10 of 83

Matching
Print the Hub Top, Hub Bottom, and both Buttons in the same color.

Different Colored Buttons
Print the buttons in a different color from the Hub Top, and optionally different from each other.

High Contrast Labels
Use a layer-based color swap so the labels are a different color than the surface of the Hub. This can be done on both the Hub Top and Hub Bottom. A second layer swap can be used to make the Hub Enclosure look consistent.

### Post-Processing

Remove any stringing or rough edges of parts with a hobby knife, seam remover, or other appropriate tool.

### Examples of Quality Prints

### Joystick

LS4_Inner_Gimbal_1.stl | LS4_Inner_Gimbal_2.stl | LS4_Outer_Gimbal_1.stl
LS4_Outer_Gimbal_2.stl | LS4_Gimbal_Shield.stl | LS4_.Gimbal_Sled.stl
LS4_Magnet_Clip.stl | LS4_Front_Cap.stl | LS4_Joystick_Housing.stl
LS4_Inner_Locking_Ring.stl | LS4_Outer_Locking_Ring.stl | LS4_Rear_Housing.stl

## MAKER GUIDE

Files available at https://github.com/makersmakingchange/LipSync | Page 11 of 83

### Hub

LS4_Hub_Bottom.stl | LS4_Hub_.stl | LS4_Hub_Next_Button.stl
LS4_Hub_Select_Button.stl | LS4_Hub_LED_Spacer.stl

## MAKER GUIDE

Part A Components; LipSync Hub PCB; QTY; Capacitor,; QTY 1; Resistor R1, 100 Ω, ¼ W, Through hole; Resistor R2/R3/R4 68 Ω, ¼ W, Through hole; QTY 3; Tactile Buttons S1/S2; QTY 2; Piezo Buzzer PS1240; Male Header, 4; position; Sparkfun QWIIC Adapter; Mono Switch Jacks

Files available at https://github.com/makersmakingchange/LipSync | Page 12 of 83

### Master Component List

## MAKER GUIDE

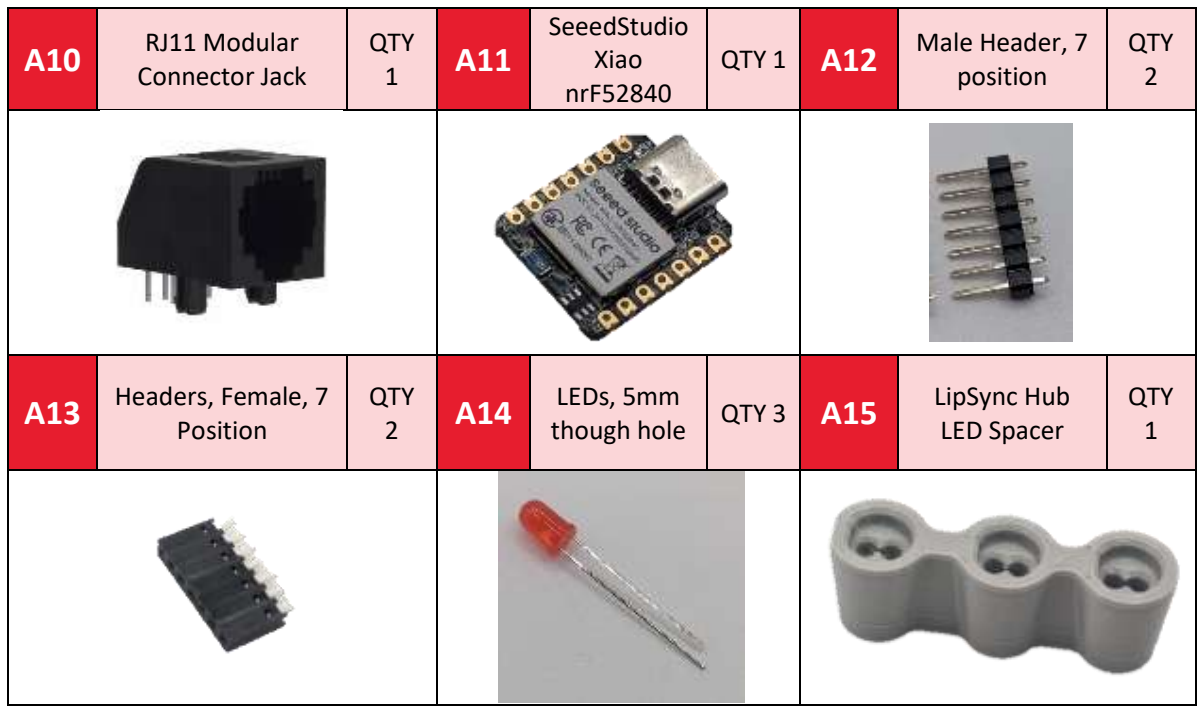
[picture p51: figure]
RJ11 Modular; Connector Jack; QTY 1; SeeedStudio Xiao nrF52840; Male Header, 7; position; QTY 2; Headers, Female, 7; Position; LEDs, 5mm; though hole; QTY 3; LipSync Hub; LED Spacer
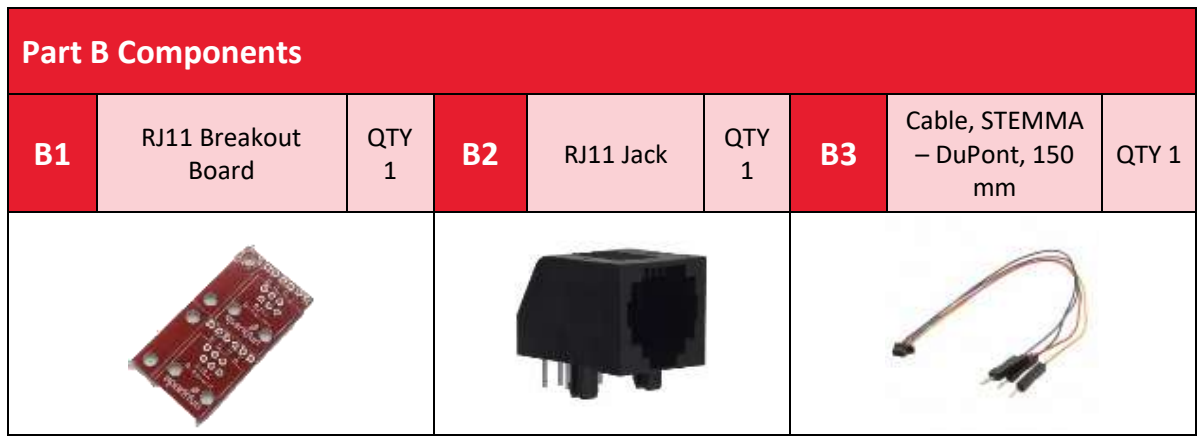
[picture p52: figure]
Part B Components; RJ11 Breakout; Board; QTY 1; RJ11 Jack; QTY; Cable, STEMMA – DuPont, 150 mm

Files available at https://github.com/makersmakingchange/LipSync | Page 13 of 83

## MAKER GUIDE

LPS22 STEMMA QT; Board; QTY 1; TLV493D STEMMA QT Board; LPS33 STEMMA; QT Board; Cable, STEMMA,; Cable, STEMMA, 50 mm

Part C Components; Populated LipSync 4 Hub PCB; QTY 1; STEMMA QT Cable – 100 mm; OLED Display

Files available at https://github.com/makersmakingchange/LipSync | Page 14 of 83

## MAKER GUIDE

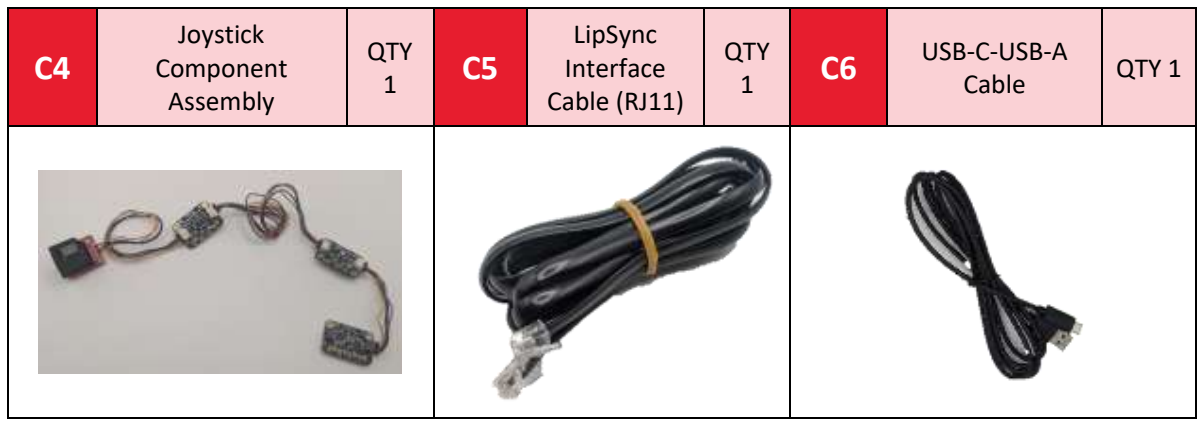
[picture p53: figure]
Joystick Component Assembly; QTY 1; LipSync Interface Cable (RJ11); USB-C-USB-A; Cable

Part D Components; Populated LipSync 4 Hub PCB; QTY 1; STEMMA QT Cable – 100 mm; OLED Display; LipSync Hub; Enclosure Top; LipSync Next Button Pusher; LipSync Select; Button Pusher

Files available at https://github.com/makersmakingchange/LipSync | Page 15 of 83

## MAKER GUIDE

Files available at https://github.com/makersmakingchange/LipSync | Page 16 of 83
D7 | LipSync Hub
Enclosure Bottom

QTY
1

D8 Screw, #4,
3/8” Length

QTY
5
D9 | M2.5 Machine
Screw, 8 mm | QTY 4
D10 | M2.5 Nut | QTY
4
D12 | Tee Nut | QTY
1
D13 | Light Pipe | QTY 1

### Part E Components

E1 | Inner_Gimbal_1 | QTY
| | 1
E2 | Inner_Gimbal_
2

QTY
1

E3 Outer_Gimbal_
1

QTY 1

E4 | Outer_Gimbal_2 | QTY
1
E5 | Gimbal Shield | QTY
1
E6 | Sled | QTY 1

## MAKER GUIDE

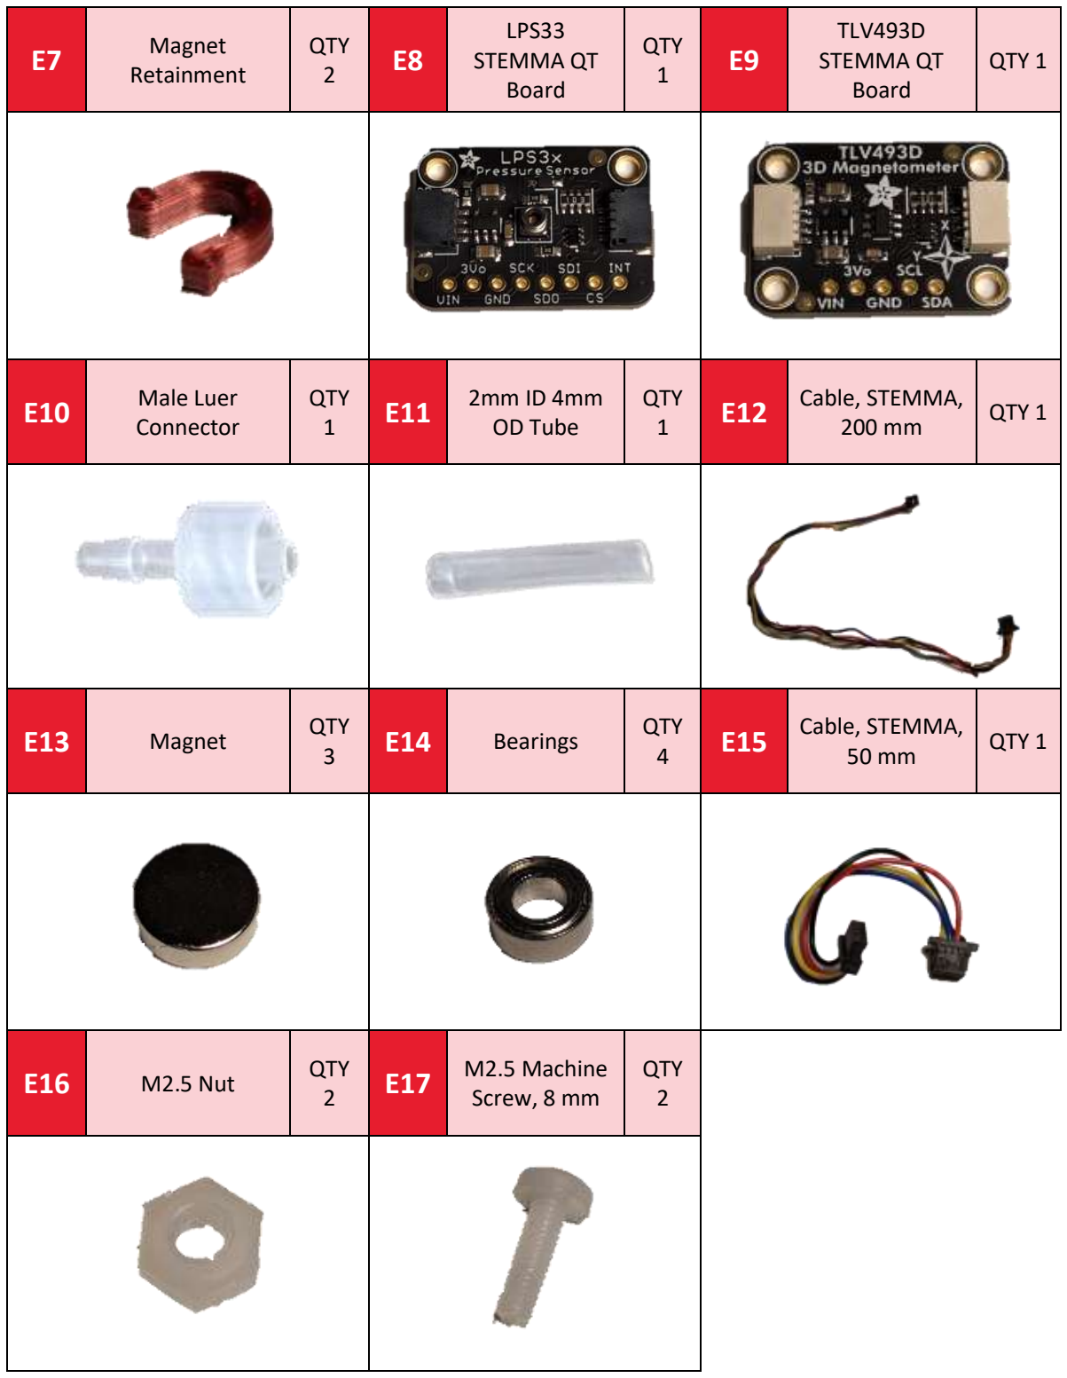
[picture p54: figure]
Magnet; Retainment; QTY 2; LPS33 STEMMA QT Board; QTY 1; TLV493D STEMMA QT Board; Male Luer; Connector; OD Tube; Cable, STEMMA,; QTY; Bearings; M2.5 Nut; M2.5 Machine; Screw, 8 mm

Files available at https://github.com/makersmakingchange/LipSync | Page 17 of 83

## MAKER GUIDE

Files available at https://github.com/makersmakingchange/LipSync | Page 18 of 83

### Part F Components

F1 | Front Cap | QTY
| | 1
F2 | Joystick
Housing

QTY
1
F3 | Inner Locking
Ring | QTY 1
F4 | Outer Locking Ring | QTY
1
F5 | Rear Housing | QTY
1
F6 | LPS22 STEMMA
QT Board | QTY 1
F7 | RJ11 STEMMA QT
Connector

QTY
1

F8

M2.5 x
Machine
Screw

QTY
1
F9 | M2.5 Nut | QTY 1

## MAKER GUIDE

Files available at https://github.com/makersmakingchange/LipSync | Page 19 of 83
F10 | Light Pipe 0.250” | QTY
1
F11 | ¼-20 Tee Nut | QTY
1

F12

Screw, #4, 3/8”
Length | QTY 3
F13 | Assembled Joystick Gimbal

QTY
1

### Part G Components

G1 | Syringe FIlter | QTY
6

G2

Mouthpiece Adapter,
1/4” Barb Connector
to Female Luer

QTY
6
G3 | Silicone Straw | QTY
2

G4 Resealable Bag

## MAKER GUIDE

Files available at https://github.com/makersmakingchange/LipSync | Page 20 of 83

## MAKER GUIDE

Files available at https://github.com/makersmakingchange/LipSync | Page 21 of 83

### Assembly Guide

The assembly of the LipSync is divided into several parts. In Part A, the Hub PCB is populated. In Part B, the joystick components are prepared. In Part C, the firmware is updated and tested with the Hub PC and Joystick components. In Part D, the Hub PCB is assembled along with other components into the Hub Enclosure. In Part E, the joystick mechanism is assembled. In Part F, the joystick mechanism is assembled into the Joystick Enclosure. In Part G, the mouthpiece components are
assembled. In Part H, the LipSync is powered on and calibrated.

It is recommended to follow the assembly instructions in the order provided. A video build guide can be found here (https://www.youtube.com/watch?v=cjADlDr1V8U) or by scanning the QR code to the right.

Assembly Section

Part A: Hub PCB Assembly

Part B: Joystick Component Preparation

Part C: Flashing Firmware

Part D: Hub Enclosure Assembly

Part E: Joystick Gimbal Assembly

## MAKER GUIDE

Files available at https://github.com/makersmakingchange/LipSync | Page 22 of 83

Part F: Joystick Housing Assembly

Part G: Mouthpiece Assembly

Error! Not a valid result for table.

## MAKER GUIDE

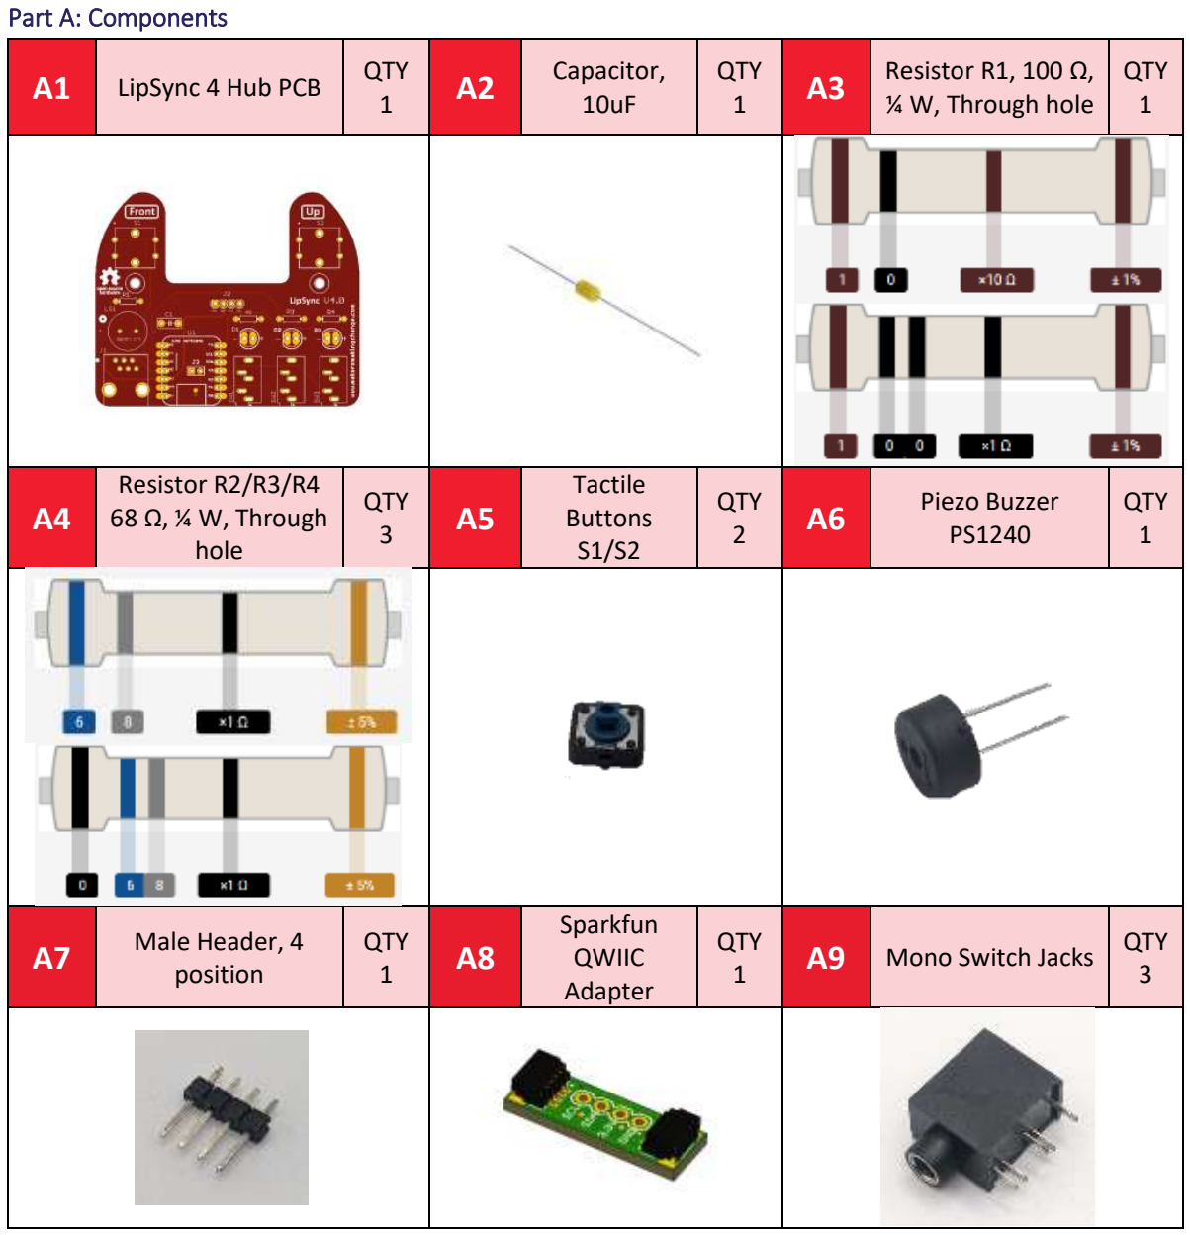
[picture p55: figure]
Part A: Components; LipSync 4 Hub PCB; QTY; Capacitor, 10uF; QTY 1; Resistor R1, 100 Ω,; ¼ W, Through hole; Resistor R2/R3/R4 68 Ω, ¼ W, Through hole; QTY 3; Tactile Buttons S1/S2; QTY 2; Piezo Buzzer PS1240; Male Header, 4; position; Sparkfun QWIIC Adapter; Mono Switch Jacks

Files available at https://github.com/makersmakingchange/LipSync | Page 23 of 83

### Part A: Hub PCB Assembly

## MAKER GUIDE

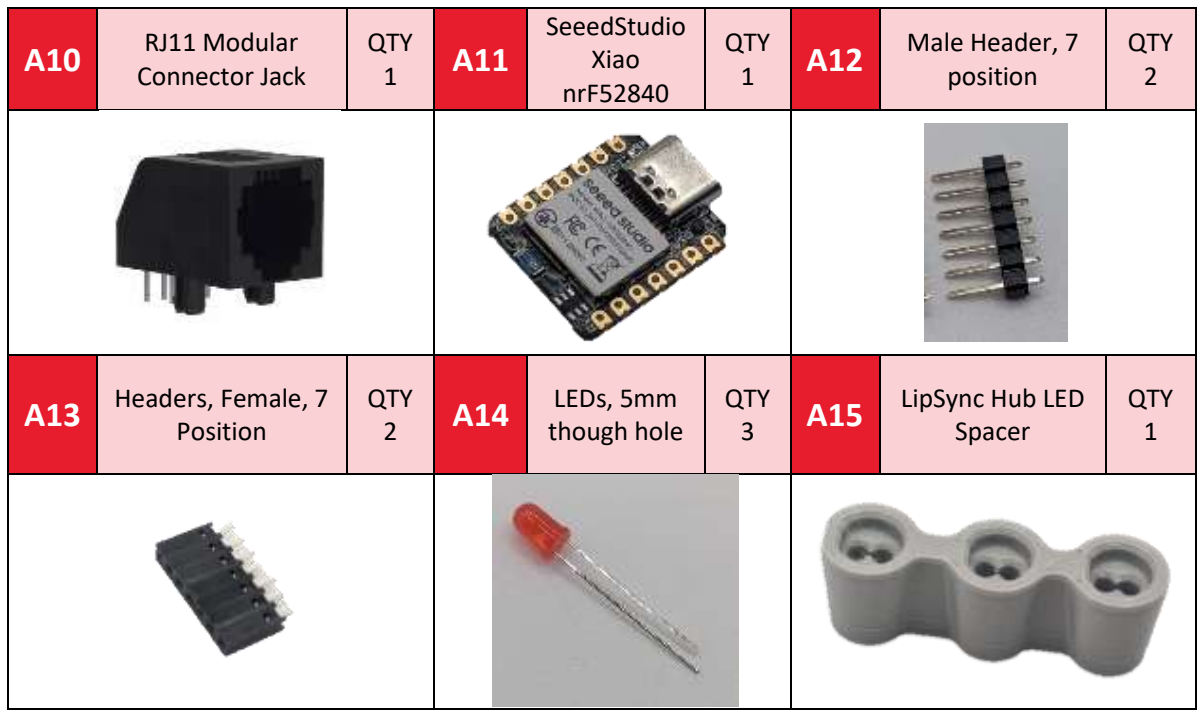
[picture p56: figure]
RJ11 Modular; Connector Jack; QTY 1; SeeedStudio Xiao nrF52840; Male Header, 7; position; QTY 2; Headers, Female, 7; Position; LEDs, 5mm; though hole; QTY 3; LipSync Hub LED; Spacer

Files available at https://github.com/makersmakingchange/LipSync | Page 24 of 83

Part A: Tools
- Soldering iron
- Flush cutters
- Phillips Head Screwdriver
- OPTIONAL: Solderless Breadboard (For soldering male headers to microcontroller)

Part A: Personal Protective Equipment (PPE)
- Safety glasses

## MAKER GUIDE

Files available at https://github.com/makersmakingchange/LipSync | Page 25 of 83

Part A: Hub PCB Assembly Steps
Note that all parts will be inserted onto the side of the PCB labeled “Front”, and all soldering will be done on the side labeled “Back”.

Step A-01: Solder in 10 micro Farad capacitor, C1.
Insert the 10 micro-Farad (µF) capacitor (A2) into the position labeled C1 on the PCB (A1). Bend the leads of the capacitor to the side to hold it in place. Solder the capacitor onto the PCB. Once soldered, trim the extra from the leads.

Step A-02: Solder in 100 Ohm resistor, R1.
Insert the 100 Ohm resistor (A3) into the position labeled R1 on the PCB. Bend the leads of the resistor to the side to hold it in place. Solder the resistor onto the PCB. Once soldered, trim the extra from the leads.

## MAKER GUIDE

Files available at https://github.com/makersmakingchange/LipSync | Page 26 of 83

Step A-03: Solder in 68 Ohm resistors, R2, R3, and R4.
Insert the 68 Ohm resistors (A4) into the positions labeled R2, R3, and R4 on the PCB. Bend the leads of the resistors to the side to hold them in place. Solder the resistors onto the PCB. Once soldered, trim the extra from the leads.

Step A-04: Insert, solder, and trim the 4-pin Male header.
Insert the longer pins of the 4-pin male header (A7) into the position labeled J2. Solder it into place and trim the excess from the bottom.

## MAKER GUIDE

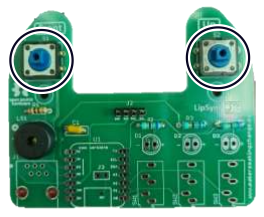
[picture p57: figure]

Files available at https://github.com/makersmakingchange/LipSync | Page 27 of 83

Step A-05: Insert, solder, and trim buzzer.
Insert the buzzer (A6) into the position labeled LS1. If using a buzzer with polarity, make sure the positive lead is in the hole marked with a “+” on the PCB. Note that the Piezo Buzzer PS1240 does not have polarity. Bend the leads to the side to hold the buzzer in place. Solder in place and trim excess from the leads.

Step A-06: Insert, solder, and trim switches.
Insert the two tactile switches (A5) into the positions labeled S1 and S2. Once soldered in place, trim any excess from leads of the switches.

## MAKER GUIDE

Files available at https://github.com/makersmakingchange/LipSync | Page 28 of 83

Step A-07: Insert and solder SparkFun QWIIC Adapter.
Place the SparkFun QWIIC Adapter (A8) on the 4-pin male header (A7) that was attached to J2 in step A-
04. Ensure the pin labels on the adapter matches the pin labels on the Hub PCB. Solder the four pins on the adapter.

Step A-08: Insert and solder switch jacks.
Insert the switch jacks (A9) into the positions labeled SW1, SW2, and SW3. Solder one pin on each switch jack, then check the alignment. If the alignment needs to be changed, reheat the solder joint until the solder melts, then reposition the jack. Once the jacks are positioned properly, solder the remaining pins.

## MAKER GUIDE

Files available at https://github.com/makersmakingchange/LipSync | Page 29 of 83

Step A-09: Solder male headers onto microcontroller.
Insert the short side of the male headers (A12) into the SeeedStudio Xiao nrf52840 microcontroller (A11) from the bottom of the board. To align the male headers and keep them straight when soldering, take the 7-position female headers (A13), and insert the male headers into the female headers across the microcontroller (as shown in the picture on the left).

Alternatively, a solderless breadboard can be used, plug the unsoldered microcontroller and headers into the protoboard and the protoboard will hold the headers in the proper alignment.

Solder the male headers onto the microcontroller, making sure not to connect adjacent pads together with solder. Once soldered, remove the 7-pin female headers from the male headers.

Step A-10: Solder female microcontroller header into PCB.
Insert microcontroller with male headers into the female headers (A13). Insert the female headers into PCB. Solder 1 pin on each header. Check alignment and adjust if necessary. If you need to adjust the alignment, heat the single soldered pin until the solder melts again and adjust the position of the row of headers. Once aligned, solder remaining headers.

## MAKER GUIDE

Files available at https://github.com/makersmakingchange/LipSync | Page 30 of 83

Step A-11: Insert and solder the RJ11 jack.
Insert the RJ11 jack (A10) into the position labeled J1 on the PCB. Solder the six pins into place.

Step A-12: Insert, solder, and trim LEDS.
Insert the three LEDs (A14) into the 3D printed LED Spacer(A15). Ensure the shorter lead of the LED (the negative lead) is on the same side as the flat edge of the LED Spacer. The LED will also have a flat edge matching the flat edge on the spacer.

With the LEDs inserted into the spacer, insert the LEDs into the matching holes in the PCB. The flat side of the LED spacer should be on the left with the rounded side on the right, when looking at the PCB from the front. Solder the LEDs in place and trim the excess from the leads.

## MAKER GUIDE

Files available at https://github.com/makersmakingchange/LipSync | Page 31 of 83

Part A Complete

## MAKER GUIDE

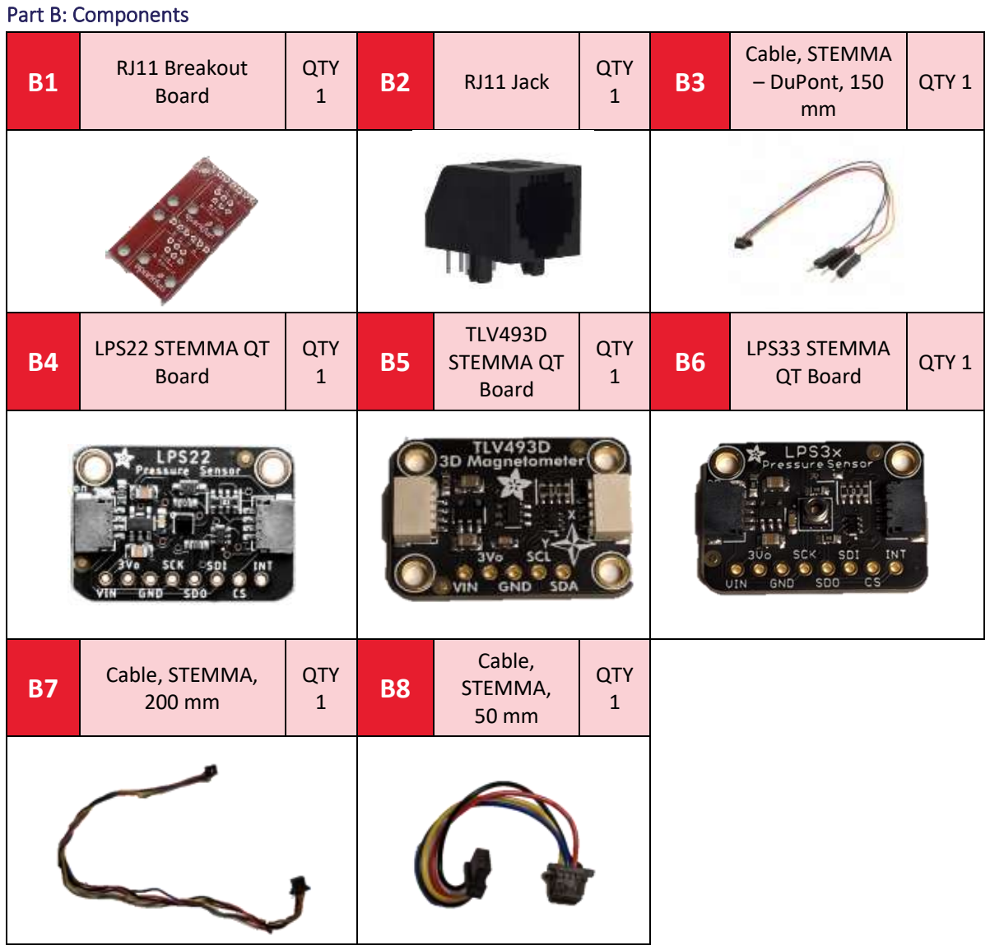
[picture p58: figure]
Part B: Components; RJ11 Breakout; Board; QTY 1; RJ11 Jack; QTY; Cable, STEMMA – DuPont, 150 mm; LPS22 STEMMA QT; TLV493D STEMMA QT Board; LPS33 STEMMA; QT Board; Cable, STEMMA,; Cable, STEMMA, 50 mm

Files available at https://github.com/makersmakingchange/LipSync | Page 32 of 83

### Part B: Joystick Component Preparation

Part B: Tools
- Soldering Iron

Part B: Personal Protective Equipment (PPE)
- Safety Glasses

## MAKER GUIDE

Files available at https://github.com/makersmakingchange/LipSync | Page 33 of 83

Part B: Assembling Hub Enclosure Steps

Step B-01: Prepare the RJ11 Breakout Board
Separate the two RJ11 Breakout Boards (B2) by snapping them apart by hand. Make sure the thin portion with the two mounting hole remains attached. Only one is required for the build.

Step B-02: Solder the RJ11 jack to the RJ11 Breakout Board
Press the RJ11 Jack (B3) into the RJ 11 Breakout Board so the pins stick out of the numbered side. Solder the six RJ11 pins poking through the board, NOT THE NUMBERED HOLES.

## MAKER GUIDE

Files available at https://github.com/makersmakingchange/LipSync | Page 34 of 83

Step B-03: Solder the STEMMA QT Cable to the RJ11 Breakout Board
Cut the Dupont Headers off the Dupont STEMMA QT Cable (B4) and strip the insulation back 5 mm. Insert the stripped wires through the corresponding holes on the RJ11 Breakout Board from the same side as the RJ11 Connector, following the order in the table. Solder in place, and trim the ends sticking out the back side.
RJ 11 Breakout | STEMMA QT Cable
2 (B) | Black (Gnd)
3 (R) | Red (Vcc)
4 (G) | Blue (SDA)
5 (Y) | Yellow (SCL)

Step B-04: Solder the pads on the back of the LPS22 Pressure Sensor Board
Use solder to create a bridge between the solder pads on the back of the LPS22 STEMMA QT Board (B5) to change the default i2C address.

## MAKER GUIDE

Files available at https://github.com/makersmakingchange/LipSync | Page 35 of 83

Step B-05: Attach the LPS22 Sensor to the RJ11 Assembly
Insert the STEMMA QT Connector from the RJ11 Assembly into one of the ports on the LPS22 Sensor.

Step B-06: Connect the Magnetic Sensor to the LPS22 Sensor using the 200 mm STEMMA Cable.
Take the 200 mm STEMMA cable (B7). Attach one end to the open port on the LPS22 Sensor and the other end to one of the ports on the Magnetic Sensor (B8).

## MAKER GUIDE

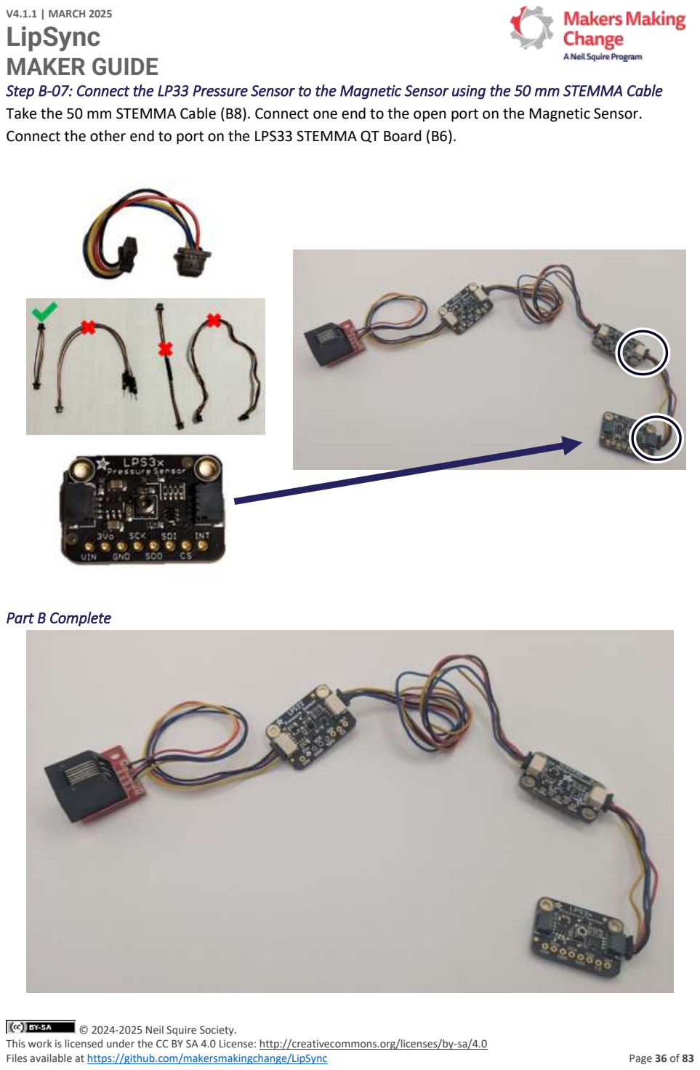
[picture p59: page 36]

Files available at https://github.com/makersmakingchange/LipSync | Page 36 of 83

Step B-07: Connect the LP33 Pressure Sensor to the Magnetic Sensor using the 50 mm STEMMA Cable Take the 50 mm STEMMA Cable (B8). Connect one end to the open port on the Magnetic Sensor. Connect the other end to port on the LPS33 STEMMA QT Board (B6).

Part B Complete

## MAKER GUIDE

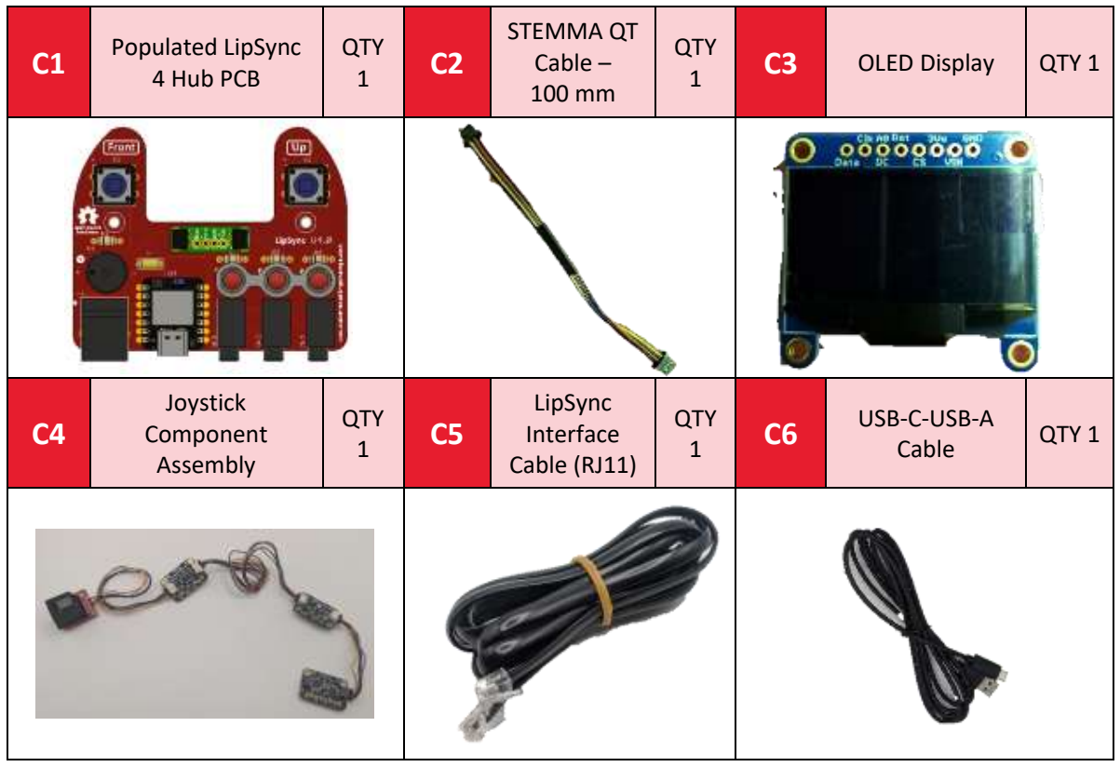
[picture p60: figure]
Populated LipSync 4 Hub PCB; QTY 1; STEMMA QT Cable – 100 mm; OLED Display; Joystick Component Assembly; LipSync Interface Cable (RJ11); USB-C-USB-A; Cable

Files available at https://github.com/makersmakingchange/LipSync | Page 37 of 83

### Part C: Flashing Firmware

Part C: Components

Part C: Tools
- Computer with Arduino IDE to flash firmware

## MAKER GUIDE

Files available at https://github.com/makersmakingchange/LipSync | Page 38 of 83

Part C: Firmware Flashing Steps

Step C-01: Connect the Display to the PCB using the 100 mm STEMMA Cable
Connect one end of the 100 mm STEMMA QT Cable (C2) into the left hand i2C connector on the LipSync Hub PCB (C1). Connect the other end of the cable into the OLED Display (C3).

Step C-02: Connect the Joystick Component Assembly to the PCB using the Interface Cable
Take the LipSync Interface Cable (C5). Connect one end to the RJ11 Connector on the PCB and one end to the RJ11 Connector on the RJ11 Connector of the Joystick Component Assembly (C4).

## MAKER GUIDE

Files available at https://github.com/makersmakingchange/LipSync | Page 39 of 83

Step C-03: Connect the LipSync Hub PCB to the Computer
Plug in the Hub PCB (C1) to a computer using the USB Cable (C6).

Step C-04: Setup Arduino IDE on Computer
1. Download Arduino IDE for your operating system at https://www.arduino.cc/en/software
2. Install the Arduino IDE.

Step C-05: Setup Arduino IDE for Seed Studio Xiao nRF52840 Development Board
1. Open Arduino IDE.
2. Click on File -> Preferences.
3. Locate the text field that says Additional Boards Manager URLs beside it.
4. Copy and paste the following link into the field as a new line:

https://files.seeedstudio.com/arduino/package_seeeduino_boards_index.json

3. Click on OK.
5. Restart the Arduino IDE.
6. Open the Boards Manager option from the Tools-> Board-> Boards Manager...,
7. Search for “Seeed nrf52” and select “Seeed nRF52 Boards” by Seeed Studio.
8. Click Install to install the board.

Step C-06: Install Libraries
1. In the Arduino IDE, go to Tools -> Manage Libraries…
2. For each of the libraries in the table below, search for the name, and click Install. If prompted to install any dependent libraries, click OK.
Name | Author
Adafruit_LPS2X | Adafruit
Adafruit_LPS35HW | Adafruit
Adafruit_SSD1306 | Adafruit
ArduinoJson | Benoit Blanchon
Adafruit_TinyUSB | Adafruit
3. Directly download the compressed zip file for the TLV493D-A1B6 Library:
a. https://github.com/Infineon/TLV493D-A1B6-3DMagnetic-Sensor/archive/refs/heads/master.zip (https://github.com/Infineon/TLV493D-A1B6-3DMagnetic-Sensor/archive/refs/heads/master.zip)
4. In the Arduino IDE, go to Sketch -> Include Library -> Add .ZIP Library… When the dialog box opens, navigate to where the library ZIP file was downloaded in the previous step, select it, and press and select the library downloaded in the previous step.

## MAKER GUIDE

Files available at https://github.com/makersmakingchange/LipSync | Page 40 of 83

Step C-07: Setup Local Code Directory
1. Download the Firmware_Files from the GitHub Repository: https://github.com/makersmakingchange/LipSync/blob/main/Build_Files/Firmware_Files/LipSync_Firmware.zip (https://github.com/makersmakingchange/LipSync/blob/main/Build_Files/Firmware_Files/LipSync_Firmware.zip)
2. Extract / unzip the folder to a known location.
3. Confirm that you have the following folder structure:
- LipSync_Firmware (folder)
- LipSync_Firmware.ino
- LSAPI.ino
- LSTest.ino
- LSBLE.h
- LSBuzzer.h
- LSCircularBuffer.h
- LSConfig.h
- LSInput.h
- LSJoystick.h
- LSMemory.h
- LSOutput.h
- LSPressure.h
- LSScreen.h
- LSTimer.h
- LSUSB.h
- LSUtils.h
- LSWatchdog.h

Step C-08: Upload the Code to the microcontroller.
1. Open LipSync_Firmware.ino with Arduino IDE.
2. Select Seeed Xiao NRF52840 from Tools -> Board -> Seeed NRF52 Boards
3. Connect the LipSync using the USB cable to the computer.
4. Select the correct port from Tools -> Port menu.
5. Verify and upload the code.

Step C-09: Verify the PCB and Sensors work as expected.
When the USB cable is connected, a green LED should illuminate on each of the sensors and the back of the display.

Once the code is uploaded, the LipSync should play the startup noise, the 3 LEDs on the Hub should turn on briefly, and the display should show the splash screen, with the words “LipSync” the version number, and “Makers Making Change”.

If all goes well, proceed to the next step. If there are any problems or errors on the display, unplug the USB cable and proceed to troubleshooting.

Step C-10: Remove the USB cable from the Hub PCB
Remove the USB cable from the Hub PCB to disconnect the power.

## MAKER GUIDE

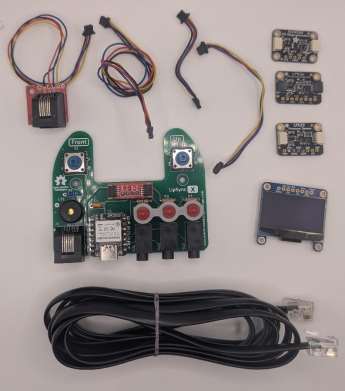
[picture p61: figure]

Files available at https://github.com/makersmakingchange/LipSync | Page 41 of 83

Step C-11: Disassemble the Joystick Component Assembly and Display
Unplug the LipSync Interface Cable from the Joystick Component Assembly and the Hub PCB. Carefully unplug the STEMMA QT Cable from the Display and the Hub PCB.

Carefully unplug the STEMMA QT Cables from each of the three sensors.

## MAKER GUIDE

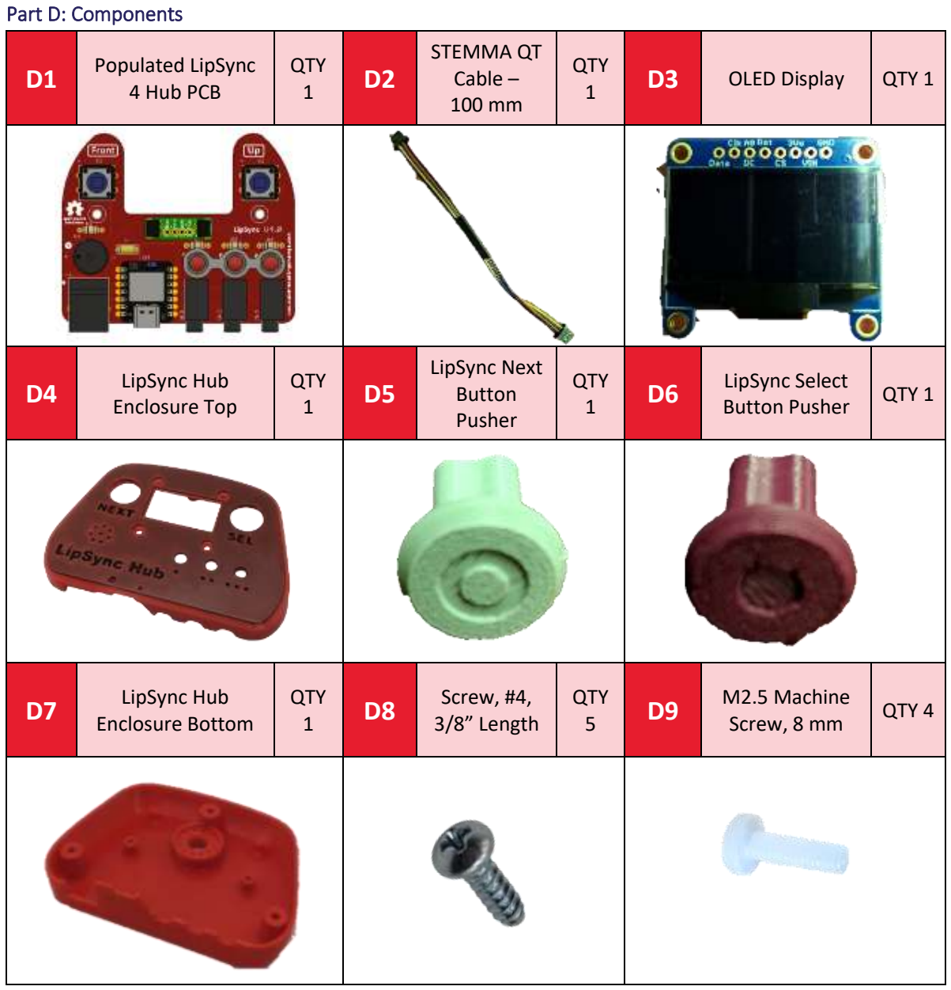
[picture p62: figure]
Part D: Components; Populated LipSync 4 Hub PCB; QTY 1; STEMMA QT Cable – 100 mm; OLED Display; LipSync Hub Enclosure Top; LipSync Next Button Pusher; LipSync Select; Button Pusher; LipSync Hub Enclosure Bottom; Screw, #4, 3/8” Length; QTY 5; M2.5 Machine; Screw, 8 mm; QTY 4

Files available at https://github.com/makersmakingchange/LipSync | Page 42 of 83

### Part D: Hub Enclosure Assembly

## MAKER GUIDE

Files available at https://github.com/makersmakingchange/LipSync | Page 43 of 83
D10 | M2.5 Nut | QTY
4
D12 | Tee Nut | QTY
1
D13 | Light Pipe | QTY 1

Part D: Tools
- Phillips Head Screwdriver

Part D: Personal Protective Equipment (PPE)
- Safety glasses

## MAKER GUIDE

Files available at https://github.com/makersmakingchange/LipSync | Page 44 of 83

Part D: Assembling Hub Enclosure Steps

Step D-01: Connect Display to LipSync 4 Hub Enclosure Top
Peel off the protective film on the Display (D3) and connect it to the Hub Enclosure Top (D4) using four nylon M2.5 machine screws (D9) and four nylon M2.5 hex nuts (D10). Do not overtighten.

Step D-02: Insert the Light Pipe
From the front side, insert the light pipe (D13) into the Hub Enclosure Top.

## MAKER GUIDE

Files available at https://github.com/makersmakingchange/LipSync | Page 45 of 83

Step D-03: Connect STEMMA / QWIIC Cable to Display
Flip the Hub Top over so the Display is facing down. Connect the 100 mm STEMMA/QWIIC cable (D2) to the port on the right-hand side of the Display as shown. Ensure the holes for the pins in the cable line up with the pins in the port on the PCB. Do not connect the second end of the STEMMA/QWIIC cable to the second port on the screen.

Step D-04: Insert the Tee Nut into the Hub Bottom
Insert the tee nut (D12) into the slots inside the Hub Bottom. A ¼” machine screw or hex bolt can be used to tighten the Tee Nut into place. The nut should sit flush with the enclosure.

## MAKER GUIDE

Files available at https://github.com/makersmakingchange/LipSync | Page 46 of 83

Step D-05: Secure LipSync Hub PCB into Hub Bottom
Use two #4 sheet metal screws (D8) to secure the PCB (D1) into the Hub Bottom.

Step D-06: Connect the STEMMA / QWIIC Cable to the QWIIC Adapter on the PCB
Connect the 100 mm STEMMA/QWIIC cable from the display to the QWIIC adapter on the PCB. Again, ensure the holes for the pins in the cable line up with the pins in the port on the PCB.

## MAKER GUIDE

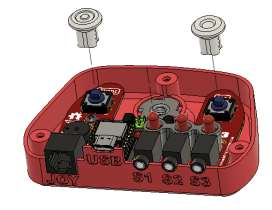
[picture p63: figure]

Files available at https://github.com/makersmakingchange/LipSync | Page 47 of 83

Step D-07: Place the Button Pushers on top of the Buttons
Position the Select Button (D6) and the Next Button (D5) on top of the Buttons on the PCB. The Next Button goes on the left button and has a target shape on the front. The Select Button goes on the right button and has a ring printed on the front.

Step D-08: Position the Hub Top on to the Hub Bottom
Position the Hub Top onto the Hub Bottom, making sure to align the Button Pushers and their LEDs with the corresponding hole.

## MAKER GUIDE

Files available at https://github.com/makersmakingchange/LipSync | Page 48 of 83

Step D-09: Secure the Hub Top and Hub Bottom
Carefully turn the Hub over. Use a #4 sheet metal screw (D8) in each of the three holes to secure the two parts together.

Part D Complete

## MAKER GUIDE

Part E: Components; Inner_Gimbal_1; QTY; Inner_Gimbal_ 2; QTY 1; Outer_Gimbal_ 1; Outer_Gimbal_2; Gimbal Shield; Sled; Magnet Retainment; QTY 2; LPS33 STEMMA QT Board; TLV493D STEMMA QT Board

Files available at https://github.com/makersmakingchange/LipSync | Page 49 of 83

### Part E: Joystick Gimbal Assembly

## MAKER GUIDE

Files available at https://github.com/makersmakingchange/LipSync | Page 50 of 83
E10 | Male Luer
Connector

QTY
1

E11 2mm ID 4mm
OD Tube

QTY
1

E12 Cable, STEMMA,
200 mm

QTY 1

E13 | Magnet | QTY
3
E14 | Bearings | QTY
4

E15 Cable, STEMMA,
50 mm

QTY 1

E16 | M2.5 Nut | QTY
| | 2
E17 | M2.5 Machine
Screw, 8 mm

QTY
2

Part E: Tools
- Phillips Head Screwdriver
- Scissors
- Flush cutters
- OPTIONAL: File or coarse sandpaper

Part E: Personal Protective Equipment (PPE)
- Safety glasses

## MAKER GUIDE

Files available at https://github.com/makersmakingchange/LipSync | Page 51 of 83

Part E: Joystick Gimbal Assembly Steps
The rulers shown in this section are to-scale so can be used to measure the required lengths of each part.

Step E-01: Cut the Tubing to length
Cut a 1.5 cm length of tubing (E11).

Step E-02: Connect the tubing to the Luer connector
Push the tubing over the barb on the Luer connector(E10), until about 2 mm is past the barb.

Step E-03: Connect the tubing to the Pressure Sensor
Press the other end of the tubing over the circular port on the LPS33 Pressure Sensor (E8).

## MAKER GUIDE

Files available at https://github.com/makersmakingchange/LipSync | Page 52 of 83

Step E-04: Attach the Tubing Assembly to the Joystick
Take the Inner Gimbal 1 3D print (E1) and press the Luer connector assembly into the slot at the front by the threads. The Luer connector must be inserted so there is a flat edge along the top and bottom, as seen in the photo on the right. The tube length should be such that the pressure sensor fits into the first slot behind the bearing shafts. When viewing the assembly from the front, the text on the sensor should be on the side facing the bearing shafts.

Step E-05: Attach the Magnetic Sensor
Slide the Magnetic Sensor (E9) into the Inner Gimbal 1 so that it is arranged back-to-back with the pressure sensor with the text facing to the left. The two sensors should have the same up/down orientation, with the text at the top, and the breakout pins at the bottom.

Secure the two sensors in place by inserting a nylon M2.5 machine screws (E17) into the left-most hole in the Pressure Sensor board, through the hole in the Inner Gimbal and through the hole in the Magnetic Sensor. Loosely attach the nylon hex nut (E16), but do not fully tighten.

## MAKER GUIDE

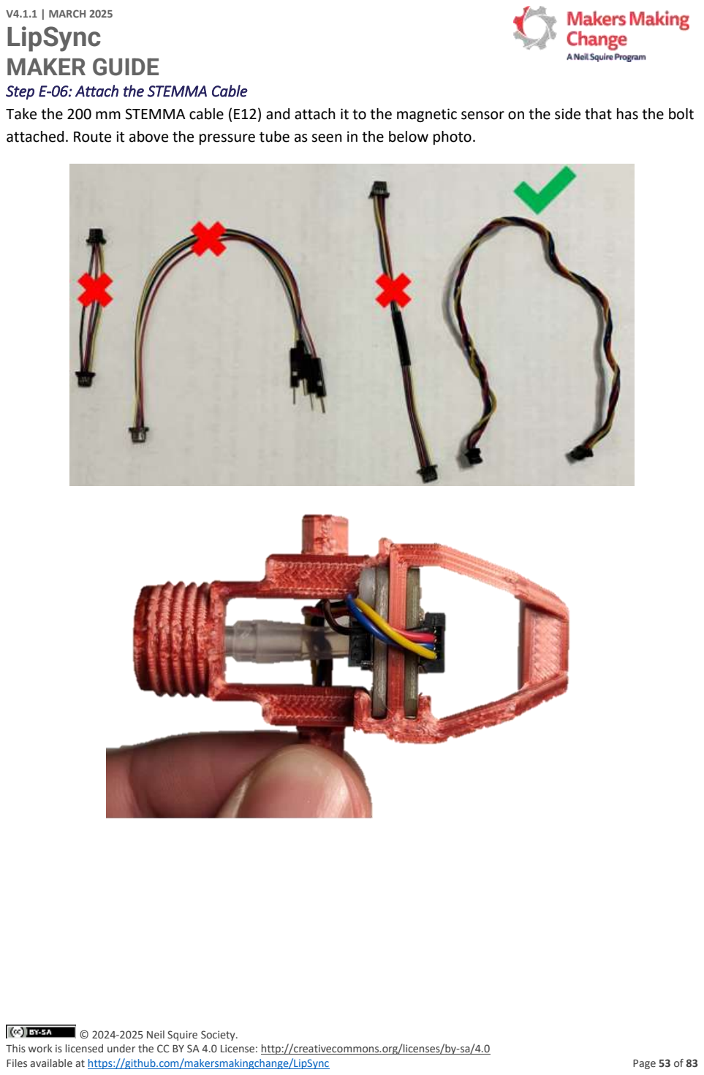
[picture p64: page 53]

Files available at https://github.com/makersmakingchange/LipSync | Page 53 of 83

Step E-06: Attach the STEMMA Cable
Take the 200 mm STEMMA cable (E12) and attach it to the magnetic sensor on the side that has the bolt attached. Route it above the pressure tube as seen in the below photo.

## MAKER GUIDE

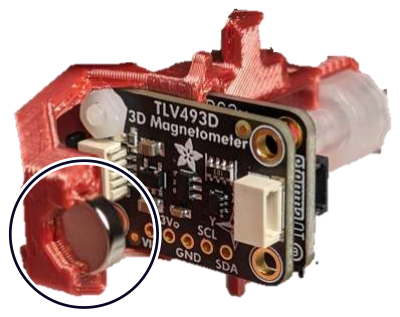
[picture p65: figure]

Files available at https://github.com/makersmakingchange/LipSync | Page 54 of 83

Step E-07: Route the cable out of the Inner Gimbal
Route the cable over the air path, and through the slot in the bearing shaft as seen in the photo.

Step E-08: Insert the Moving Centering Magnet
Gently press a magnet (E13) into the cradle in the very back of the assembly. The orientation of the magnet does not matter in this step.

## MAKER GUIDE

Files available at https://github.com/makersmakingchange/LipSync | Page 55 of 83

Step E-09: Attach the other half of the Inner Gimbal
Slide Inner Gimbal 2 (E2) over the assembly. Make sure that the Luer connector, sensor boards, and magnet line up with their corresponding slots.

Step E-10: Attach the second Machine Screw and Nut
Add the second nylon nut (E16) and bolt (E17) in the same orientation as the first, and fully tighten them both.

## MAKER GUIDE

Files available at https://github.com/makersmakingchange/LipSync | Page 56 of 83

Step E-11: Trim the edges of the STEMMA Cable Connector
Take the free end of the 200 mm STEMMA cable that exits the Inner Gimbal Assembly and trim the two flanges on the end of the connector flush.

Step E-12: Attach Bearings to the Inner Gimbal
Press one bearing (E14) over each of the two bearing shafts on the inner gimbal. For the shaft with the cable coming out, pass the cable through the inside of the bearing before placing it on the shaft.

Note: If you are having trouble getting the bearings to fit on the shafts, first try sanding down the corners of the octagonal shafts. If they still do not fit, use pliers to gently press them onto the shaft.

WARNING: Do not hit the bearings with a hammer or mallet. Do not hit the gimbal on the table or any other hard surface.

## MAKER GUIDE

Files available at https://github.com/makersmakingchange/LipSync | Page 57 of 83

Step E-13: Connect the Pressure Sensor and Magnetic Sensor
The 50 mm STEMMA Cable (E15) is used to connect the Pressure Sensor to the Magnetic Sensor. First, connect one end of the STEMMA Cable to the open connector on the Pressure Sensor Board. Next, wrap the cable around the post of the Inner Gimbal. Finally, attach the other end of the STEMMA Cable to the connector on the Magnetic Sensor Board on the same side as the Pressure Sensor.

## MAKER GUIDE


Files available at https://github.com/makersmakingchange/LipSync | Page 58 of 83

Step E-14: Assemble the Outer Gimbal on to the Inner Gimbal Assembly
Take Outer Gimbal 1 (E3, marked with “I”) and coming from the magnet side towards the Luer connector side, pass it over the Inner Gimbal Assembly. One side of the bearing cover will be hollow, and one will be covered. Align the outer gimbal so that the hollow side is on the same bearing that the STEMMA cable is passing through.

Step E-15: Route cable through the Outer Gimbal
Pass the cable through the slot on the outer gimbal, and then out through the hollow bearing shaft. A pair of tweezers can be used to push the wires into the slot.

## MAKER GUIDE

Files available at https://github.com/makersmakingchange/LipSync | Page 59 of 83

Step E-16: Connect the second half of the Outer Gimbal
Press the front half of the Outer Gimbal (Outer Gimbal 2, E4, marked with “II”) over the front Luer section and towards the rear, ensuring that the cable is properly connected to the correct cable management slots.

Step D-17 Secure Outer Bearing to Gimbal
Secure the two halves of the Outer Gimbal using two bearings (D14). Gently pull on the cable after the bearings are attached to remove any slack.

## MAKER GUIDE

Files available at https://github.com/makersmakingchange/LipSync | Page 60 of 83

Step E-18: Screw on the Gimbal Shield
Take the Gimbal Shield (E5) and screw it onto the threads at the front of the gimbal until it hits the gimbal hard stop at the back.

Step E-19: Insert Magnets into Sled
Take the Sled (E6), and two Magnets (E13). Stick the two magnets to either side of the gimbal magnet from the previous steps, and make note of their orientation. While keeping them in the same orientation, gently but firmly push them into the two highlighted slots in the sled, until they are firmly seated at the bottom of the slots. It is very important to seat these magnets at the bottom of the slots.

## MAKER GUIDE


Files available at https://github.com/makersmakingchange/LipSync | Page 61 of 83

Step E-20: Secure the Magnets into the Sled
With the magnets pushed down fully, push a Magnet Clip (D7) into each of the Sled slots to secure the magnets in place.

Step E-21: Place Gimbal Assembly in the Sled
Slot the Gimbal into the Sled. Slot the magnet in the back of the gimbal between the two towers on the sled, and then gently attach the arms to the bearings. One side of the sled has a cover over the bearing slot and one side has an open bearing slot. The side of the gimbal with the cables coming out of it lines up with the open bearing slot with no cover.

## MAKER GUIDE


Files available at https://github.com/makersmakingchange/LipSync | Page 62 of 83

Step E-22: Route the STEMMA Cable through the Sled
Take the STEMMA Cable that is leaving the gimbal through the bearing, and thread it through slot on the sled, then clip it into the ¾ circle at the bottom of the sled, as seen in the below photos.

Part E Complete

## MAKER GUIDE

Files available at https://github.com/makersmakingchange/LipSync | Page 63 of 83

### Part F: Joystick Housing Assembly

Part F: Components

F1 | Front Cap | QTY
| | 1
F2 | Joystick
Housing

QTY
1
F3 | Inner Locking
Ring | QTY 1
F4 | Outer Locking Ring | QTY
1
F5 | Rear Housing | QTY
1
F6 | LPS22 STEMMA
QT Board | QTY 1
F7 | RJ11 STEMMA QT
Connector

QTY
1

F8

M2.5 x
Machine
Screw

QTY
1
F9 | M2.5 Nut | QTY 1

## MAKER GUIDE

Light Pipe 0.250”; QTY; ¼-20 Tee Nut; QTY 1; Screw, #4, 3/8”; Length; QTY 3; Assembled Joystick Gimbal

Files available at https://github.com/makersmakingchange/LipSync | Page 64 of 83

Part F: Tools
- Phillips Head Screwdriver

Part F: Personal Protective Equipment (PPE)
- Safety glasses

## MAKER GUIDE

printed above it.

Files available at https://github.com/makersmakingchange/LipSync | Page 65 of 83

Part F: Assembling Joystick Housing Steps

Step F-01: Insert the Light Pipe into the Joystick Housing
From the outside, press the light pipe (F10) into the Joystick Housing (F2). You can use a table or a hard surface to slowly press against to push the Light Pipe into place.

Step F-02: Connect the LPS22 Sensor Board to the gimbal STEMMA QT Cable
Connect the STEMMA QT cable coming from the gimbal (F13) to the LPS22 board. Ensure it is connected to the left port when viewing the board right-side up from the front. This is the port that has “on”

## MAKER GUIDE

Files available at https://github.com/makersmakingchange/LipSync | Page 66 of 83

Step F-03: Insert the LPS22 board into the Joystick Housing
Entering through the larger opening (side with internal threads) of the joystick housing, snap (not slide) the LPS22 board into place directly below the light pipe so that the cable points toward the opening you just entered the part through. The components on the board should be facing towards the outer wall of the 3D print, not the hollow middle.

Step F-04: Route the Cable
Route the cable from where it connects to the LPS22 Sensor Board beside the board and towards the rear of the Joystick Housing. Insert the cable into the snap-fit beside the board.

## MAKER GUIDE


Files available at https://github.com/makersmakingchange/LipSync | Page 67 of 83

Step F-05: Insert the Gimbal Subassembly into the Joystick Housing
Entering through the same side as step 4, line up the sled so it will slot into the rails at the rear end of the joystick housing and slide it into place. Be careful to keep the STEMMA QT cable from getting pinched between printed parts.

## MAKER GUIDE

Files available at https://github.com/makersmakingchange/LipSync | Page 68 of 83

Step F-06: Screw on the Front Cap
Ensure the joystick is fully inserted and the cable is not interfering with any internal parts. Screw on the front cap (F1) by rotating clockwise.

Step F-07: Insert the Tee Nut
Insert the Tee Nut (F11) into the hole in the Rear Housing. Line up the prongs with the slots and press the Tee Nut into the Rear Housing until the bottom is flush.

Note: Once the Tee Nut is aligned, a ¼-20 UNC bolt or machine screw can help pull the Tee Nut down into place. Insert the bolt or machine screw into the Tee Nut and tighten until the bottom of Tee Nut is flush with the bottom of the print. Make sure to remove the bolt once the Tee Nut is installed.

## MAKER GUIDE

Files available at https://github.com/makersmakingchange/LipSync | Page 69 of 83

Step F-08: Insert the Captive Nut into Rear Housing
Insert a M2.5 nylon nut (F9) into the captive nut slot shown on the Rear Housing (F5).

Step F-09: Insert and fasten the RJ11 Breakout Board into the Rear Housing
Slide the RJ11 Breakout Board in the slot in the back of the Rear Housing. Secure it in place with a nylon M2.5 machine screw (F8) into the captive nut.

## MAKER GUIDE

Files available at https://github.com/makersmakingchange/LipSync | Page 70 of 83

Step F-10: Nest the locking rings
Take the Inner (F3) and Outer (F4) Locking Rings, and pass the Inner Ring through the Outer Ring until it has gone as far as it can go as seen in the below photos. The flat print face should be facing the same direction on each piece. The Inner Ring has a tab, and the Outer Ring has a slot. The only way for the rings to fit together is for the tab on the Inner Ring to be aligned with the slot on the Outer Ring, as seen in the photos.

## MAKER GUIDE


Files available at https://github.com/makersmakingchange/LipSync | Page 71 of 83

Step F-11: Fasten Locking Rings to Rear Housing
As with the previous step, there is a slot on the rear housing that lines up with the tab on the Inner Locking Ring. If this is done correctly, the three holes on the inner ring will line up with the three holes on the rear housing. Using #4 3/8 (F12) screws, fasten the locking rings onto the rear housing.

Step F-12: Connect the Dupont to Stemma cable to the Ambient Pressure Sensor Board.
Plug the STEMMA QT end of the STEMMA-DuPont cable into the open port of the LPS22 board at the rear of the joystick housing.

## MAKER GUIDE

Files available at https://github.com/makersmakingchange/LipSync | Page 72 of 83

Step F-13: Connect the two halves of the Joystick Housing
Screw the locking ring from the back section of the enclosure to the threads on the front half of the enclosure. Tighten the locking ring until the two halves are locked together. Be careful to not rotate the two halves relative to each other so the STEMMA-DuPont cable does not get twisted.

## MAKER GUIDE

Files available at https://github.com/makersmakingchange/LipSync | Page 73 of 83

Part F Complete: Joystick Unit Assembled

## MAKER GUIDE

Files available at https://github.com/makersmakingchange/LipSync | Page 74 of 83

### Part G: Mouthpiece Assembly

Part G: Components

G1 | Syringe FIlter | QTY
6

G2

Mouthpiece Adapter,
1/4” Barb Connector
to Female Luer

QTY
6
G3 | Silicone Straw | QTY
2

G4 Resealable Bag

Part G: Tools
- Scissors or Hobby Knife

Part G: Personal Protective Equipment (PPE)
- Safety glasses

## MAKER GUIDE

Files available at https://github.com/makersmakingchange/LipSync | Page 75 of 83

Part G: Assembling the Mouthpiece Steps

Step G-01: Prepare a clean work surface.
Since the mouthpieces are intended a user’s mouth, the parts (except for the filter) should be washed beforehand using dish detergent. Mouthpiece assembly should be performed on a clean dry surface, such as a cutting board, suitable for food preparation.

Step G-02: Cut the Silicone Straw to length
Cut the silicone straw (G3) to 28 mm length. The rulers shown below is to-scale and can be used to measure the required length.

Repeat this step 6 times.

Step G-03: Slide the Silicone Straw on to the Mouthpiece Tube Adapter
Slide the cut length of silicone straw over the barb connection on the Luer Fitting (G2).

Repeat this step 6 times.

## MAKER GUIDE


Files available at https://github.com/makersmakingchange/LipSync | Page 76 of 83

Step G-04: Attach the Mouthpiece Adapter to the Filter
Insert the male Luer of the filter into the female Luer portion of the mouthpiece adapter. Push it as far down as possible using a twisting motion.

Repeat this step 6 times.

Step G-05: Store the mouthpieces in a clean container.
Take the 5 mouthpieces intended for the user and place them within a clean sealable bag. The final mouthpiece can be used by the maker for initial testing and calibration.

## MAKER GUIDE

Files available at https://github.com/makersmakingchange/LipSync | Page 77 of 83

Part G Complete

## MAKER GUIDE

Files available at https://github.com/makersmakingchange/LipSync | Page 78 of 83

### Part H: Initial LipSync Setup and Testing

Part H: Initial LipSync Setup Steps

Step H-01: Connect the Mouthpiece to the Joystick
Hold the mouthpiece (H2) by the outer edge of the filter, put it in the Luer connector on the LipSync (H1) and gently twist to make a connection. Twist until finger tight.

Step H-02: Connect the LipSync to Host Device using USB Cable
1. Plug in the Joystick to the Hub via the RJ 11 Cable.
2. Plug in the Hub to a computer via USB cable.
3. The Hub should power on with a startup tone and display the current code version and operating mode on the Hub display screen.

## MAKER GUIDE

Files available at https://github.com/makersmakingchange/LipSync | Page 79 of 83

Step H-03: Calibrate the Joystick
NOTE: Use the extra mouthpiece to perform the calibration to ensure the user receives a clean mouthpiece.
1. Enter the settings menu by:
a. Short press (<1 seconds) Next and Select on the Hub simultaneously.
b. Holding down the “Next” button on the Hub for at least five seconds.
2. Use the “Next” and “Select” buttons to navigate to the Calibrate menu and select it.
3. In the submenu, select “Full Calibration” and follow the prompts that appear on the Hub Display to calibrate the joystick. Detailed instructions can be found in the User Guide.

## MAKER GUIDE

Files available at https://github.com/makersmakingchange/LipSync | Page 80 of 83

### Testing Guide

After building the LipSync Hub and Joystick, you must verify both units are functioning properly.

### Testing the LipSync

1. Does Display turn on?
a. Ensure that the LipSync joystick in plugged into the Hub using the RJ11 cable.
i. Ensure that the LipSync Joystick light pipe lights up green.
b. If the Hub turns off and does not work, reset the device, and open the serial monitor in Arduino IDE right after resetting to see if one of the STEMMA boards is not being recognised.

Testing Mouse Mode
Refer to the LipSync User Guide for instructions on how to connect the LipSync to a Host Device and change the operating mode to USB Mouse Mode. When in USB Mouse Mode, ensure moving the joystick moves the mouse cursor. Additionally, test the sip and puff function, external switches, and buttons on the Hub. Ensure that each sip/puff, external switch, and Hub button action are consistent with the following tables.

Testing Sip and Puff
Install one of the assembled mouthpieces to the LipSync joystick. Once you have tested and confirmed that the sip and puff functions work, dispose of the mouthpiece you used to test.

Sip
To perform a Sip Input, close your lips around the end of the mouthpiece and sip like you would a drink through a straw (i.e., inhale or apply negative pressure) for less than 1 second and then release. The Right-side Feedback light should blink once after releasing the sip input, and the mouse should perform a right click.

Puff
To perform a Puff Input, close your lips around the opening on the mouthpiece and blow air into it (i.e., exhale or apply positive pressure) for less than 1 second and then release. The Left Feedback light should blink once after releasing the puff input, and the mouse should perform a left click.
LipSync Mouthpiece Input | Joystick | Short Puff | Long Puff | Very Long Puff | Short Sip | Long Sip | Very Long Sip
Mouse Action | Cursor Movement | Left click | Start Drag Mode | Enter Hub Menu | Right Click | Start Scroll Mode | Middle Click

## MAKER GUIDE

Files available at https://github.com/makersmakingchange/LipSync | Page 81 of 83

Testing External Switches
Plug an assistive switch into the external switch jacks and activate the assistive switch. The behaviour for each switch and type of activation is outlined in the table below:
Input | Mouse | Gamepad | Menu/Settings Mode
S1 Short Press | Left Click | Button 1 press | Next
S1 Long Press | Start drag mode | Button 3 press | N/A
S1 Very Long Press | Enter settings mode | Enter settings Mode | Exit settings mode
S2 Short Press | Middle Click | Button 5 press | N/A
S2 Long Press | Middle click | Button 6 press | N/A
S2 Very Long Press | Perform Center Reset | Perform Center Reset | N/A
S3 Short Press | Right Click | Button 2 press | Select menu item
S3 Long Press | Start scroll mode | Button 4 press | N/A
S3 Very Long Press | Middle click | N/A | N/A
S1 is the left switch, S2 is the center switch, and S3 is the right switch.

Testing Hub Buttons
Ensure the following behaviours are consistent when pressing the buttons on the Hub.
LipSync Hub Button Inputs | Select Short Press | Select Long Press | Select Very Long Press | Next Short Press | Next Long Press | Next Very Long Press | Next and Select
Mouse Behaviour | Left Click | Start Drag Mode | Enter Hub Menu | Right Click | Start Scroll Mode | Middle Click | Next and Select

Input Feedback
Each LED is designated to a set of inputs:

Left LED •: Puff, Next (Hub), S1
Middle LED ••: S2
Right LED •••: Sip, Sel (Hub), S3

The time durations Short, Long, and Very Long for the Sip/Puff and switch/button inputs are the following:

Short: Less than 1 seconds. Indicated by the respective LED blinking once.
Long: Between 1 to 3 seconds. Indicated by the respective LED flashing slowing.
Very Long: 3 seconds or longer. Indicated by the respective LED flashing quickly.

Ensure the LEDs behave as outlined above.

## MAKER GUIDE

Files available at https://github.com/makersmakingchange/LipSync | Page 82 of 83

Troubleshooting
1. Arduino IDE is stuck when uploading code to the board.

You can first try to reset the board by clicking the "Reset Button" once. If that does not work, rapidly click it twice to enter bootloader mode. If that also doesn't work, disconnect the board from the PC, and connect the board again.

2. The board is not showing up as a serial device on Arduino IDE.

You can first try to reset the board by clicking the "Reset Button" once. If that does not work, rapidly click it twice to enter bootloader mode.

3. Arduino IDE states an error about Python not being found.

Install Python 3 on to the computer, restart the Arduino IDE and try again.

4. The LipSync plays an error tone and then lists an error in Safe Mode.
a. Disconnect the Hub from power.
b. Wait 15 seconds.
c. Unplug the LipSync Interface cable on both ends and plug both ends back in.
d. Reconnect the Hub to power.

If this does not resolve the error, make note of the error code on the Safe Mode menu screen, and refer to the table below:

## MAKER GUIDE

Files available at https://github.com/makersmakingchange/LipSync | Page 83 of 83

Table 3. LipSync Error Table - Makers

Error Code | Connection Error | Maker Action Display | Ambient Pressure | Mouthpiece Pressure | Joystick Sensor
ERROR-001 | | | | ● | Check that I2C cables are securely inserted into each sensor inside joystick.
ERROR-002 | | | ●
ERROR-003 | | | ● | ●
ERROR-004 | | ●
ERROR-005 | | ● | | ●
ERROR-006 | | ● | ●
ERROR-007 | | ● | ● | ● | 1. Check that the LipSync interface cable is securely connected on both ends. 2. Confirm the LipSync Interface Cable is the right type. 3. Check that the RJ11 Connector board inside the joystick has all wires connected.
ERROR-008 | ● | | | ● | Check that I2C cable is securely inserted into Display within Hub. Check that I2C cables are securely inserted into each sensor inside joystick.
ERROR-009 | ● | | ●
ERROR-010 | ● | | ● | ●
ERROR-011 | ●
ERROR-012 | ● | ● | ● | ●
ERROR-013 | ● | ● | ●
ERROR-014 | ● | ●
ERROR-015 | ● | ● | ● | ●

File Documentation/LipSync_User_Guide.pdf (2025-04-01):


© 2024-2025 by Neil Squire. (https://neilsquire.ca/) This work is licensed under the CC BY SA 4.0 License: http://creativecommons.org/licenses/by-sa/4.0 Files available at www.github.com/makersmakingchange/LipSync

# LipSync User Guide

V4.1 – March 2025

V4.1 | MARCH 2025

## LipSync

## USER GUIDE

Files available at www.github.com/makersmakingchange/LipSync | Page 2 of 51

## Table of Contents

Introduction | 4
Features | 4
Joystick Features | 5
Hub Features | 6
Specifications | 7
LipSync Compatibility | 7
Setting Up the LipSync | 8
1. Mount the LipSync Joystick | 8
2. Mount the LipSync Hub | 10
3. Connect the LipSync Joystick to the LipSync Hub | 11
4. Optional: Connect Assistive Switches to the LipSync Hub | 12
Connecting the LipSync Hub to the Host Device | 12
Powering the Device | 13
Changing the Operating Mode | 14
Connecting in USB Mouse Mode | 15
Connecting in Wireless Mouse Mode | 17
Connecting in USB Gamepad Mode | 19
Setting Up Host Device | 20
Enable On-Screen Controls | 20
Operating the LipSync | 22
How to Perform LipSync Inputs | 22
USB & Wireless Mouse Mode | 23
USB Gamepad Mode | 25
Input and Feedback Summary | 27
The Hub Menu | 30
Accessing the Hub Menu | 30
Navigating the Hub Menu | 30
Hub Menu Options | 31
Adjusting the LipSync | 34

## USER GUIDE

Files available at www.github.com/makersmakingchange/LipSync | Page 3 of 51
Center Reset | 34
Full Calibration | 35
Changing LipSync Settings | 36
Maintenance | 41
Replacing the Mouthpiece | 41
Cleaning the LipSync | 42
Frequently Asked Questions | 42
Troubleshooting | 42
Error Codes | 44
Contacting Support | 45
References | 45
Appendix A: Serial Interface (Application Programming Interface) | 46
Serial Interface Setup | 46
Sending Commands | 46
API Format LipSync 4.1 Command List | 47

## USER GUIDE


Files available at www.github.com/makersmakingchange/LipSync | Page 4 of 51

## Introduction

The LipSync is a mouth-operated sip-and-puff joystick that can emulate a mouse, wireless mouse, or gamepad to control a computer, gaming console, smart phone, or tablet. The joystick can be moved with the mouth to move a cursor or control a joystick. By sipping and puffing on the joystick mouthpiece, clicks and buttons presses can be entered.

A shorter QuickStart Guide is available (https://github.com/makersmakingchange/LipSync/blob/main/Documentation/LipSync_Quickstart_Guide.pdf) on GitHub.

## Features

LipSync Joystick: The LipSync Joystick is the interface for the primary user. It measures the movement of the mouthpiece and the pressure of sips and puffs applied to the mouthpiece.

LipSync Hub: The LipSync Hub provides user feedback through a graphical display, LEDs, and a speaker. It also has two built in buttons and provides the connection to the host device and up to three external assistive switches.

LipSync Interface Cable: The LipSync Interface Cable is an RJ11 phone cable used to connect the LipSync Joystick to the LipSync Hub.

USB Cable: The USB Cable is used to supply power to the LipSync and in some cases, act as the primary connection to the host device. The side of the cable going to the Hub must be USB-C.

Figure 1. QuickStart
Guide QR Code

## USER GUIDE


Files available at www.github.com/makersmakingchange/LipSync | Page 5 of 51

### Joystick Features

Sip and Puff Joystick: Measures the movement of and pressure applied to the mouthpiece

Filtered Mouthpiece: The mouthpiece is a consumable part that uses a hydrophobic filter to protect the interior pressure sensor. It threads on to the Sip and Puff Joystick.

Power and Orientation LED: The Power and Orientation LED signifies that the joystick is plugged into the Hub when powered and is also used to properly orient the joystick. The LED is on the very top middle on the joystick.

Rotatable Mounting: The Mounting Angle of the LipSync can be adjusted by loosening the Outer Locking Ring, rotating the Front Section, and retightening the Outer Locking Ring.

Hub Port: The Joystick plugs into the Hub using the LipSync Interface Cable.

Mounting Connection: The joystick can be mounted using the ¼-20 (standard camera mount) threads on the rear section.

## USER GUIDE


Files available at www.github.com/makersmakingchange/LipSync | Page 6 of 51

### Hub Features

Hub Display: The Hub Display allows the users to make quick adjustments to device settings, calibrate the joystick, and change the operating mode. It also displays mode and version information upon startup.

Next & Select Buttons: The Next and Select Buttons on the Hub allows a support person to access the Hub Menu without the need to use sip and puff, or the assistive switch ports.

Feedback Speaker: The Feedback Speaker gives auditory feedback through beeping tones. The sound can be turned on or off through the Hub Menu.

Feedback Lights: The Feedback Lights give visual feedback through flashing on input durations. Each light represents a specific set of inputs.

Operating Mode Indicator: The Operating Mode Indicator is used to show whether the device is in USB Mouse, Wireless Mouse, or USB Gamepad mode.

Microcontroller Reset: The Microcontroller Reset hole allows access to the reset pin on the microcontroller using a paperclip or similar sized object.

## USER GUIDE

Files available at www.github.com/makersmakingchange/LipSync | Page 7 of 51

Mounting Connection: The Hub can be mounted in view beside the host device screen so that it is easy to see/hear the feedback and read the Menu Screen when adjusting settings. The ¼-20 threads are the same as a standard camera mount.

Joystick Port: The LipSync Joystick plugs into this port using the LipSync Interface Cable.

USB Port: This port provides the device with power and can also be the direct connection to the host device.

Assistive Switch Ports: Up to 3 assistive switches with 3.5 mm audio plugs can be connected to the LipSync Hub. By default, these external switches can be used in place of the Sip and Puff controls.

## Specifications

Specification | Value
Joystick Size (Length x Width x Height) [mm] | 170 mm x 53 mm x 66 mm
Hub Size (Length x Width x Height) [mm] | 104 mm x 29 mm x 72 mm
Joystick Mass | 123 g
Hub Mass | 90 g
Power Consumption | ~0.1 W (20mA @ 5 V)
Joystick Angular Range | ± 10°
Joystick Movement Range | ± 10 mm (using standard mouthpiece)
Operating Force | ~30 grams-force

### LipSync Compatibility

The LipSync is compatible with host devices that support a USB Mouse, a Bluetooth Mouse, or a USB-HID Gamepad. This includes Windows, macOS and Linux computers, most Android and Windows phones and tablets, and Apple iOS phones and tablets with iOS13 and iPadOS. Not all mobile phones and tablets support external pointing devices like the LipSync or other mouse replacements. Check with the manufacturer before purchasing. Look to see if your device supports “USB OTG HID” or “Universal Serial Bus On-the-Go Human Interface Device” profile.

Operating
System

Compatibility per Mode
USB Mouse | Wireless Mouse | USB Gamepad
| Android | 1 | 1
| iOS²
| iPadOS
| Windows
| macOS
| Linux
| Windows

Phone/Tablet

Desktop

### 1 Only with devices with USB OTG HID (Universal Serial Bus

On-The-Go Human Interfere Device)
2 Only for iOS13+ and iPadOS.

## USER GUIDE


Files available at www.github.com/makersmakingchange/LipSync | Page 8 of 51

## Setting Up the LipSync

This section outlines the necessary steps to setup the LipSync. First, the LipSync Joystick and the LipSync Hub need to be positioned and mounted appropriately. Next, the Joystick must be connected to the Hub using the LipSync Interface Cable. Assistive Switches are then connected to the Hub if desired. Once these steps are complete, the LipSync is ready to connect to a Host Device. The following sections expand on each of these steps in more detail.

1. Mount the LipSync Joystick
2. Mount the LipSync Hub
3. Connect the LipSync Joystick to the LipSync Hub
4. Optional: Connect Assistive Switches to the LipSync Hub

### 1. Mount the LipSync Joystick

The LipSync Joystick should be mounted securely in front of the user’s face in a way that minimally obstructs their field of view. The mouthpiece should be within reach of the user’s mouth.

Warning: The LipSync Joystick contains 3 rare earth magnets. Do not mount the joystick within 6 inches of any implanted medical devices, such as pacemakers. [1]

The LipSync Joystick has a female ¼”-20 UNC threaded mounting connection. This type of connection is compatible with a variety of commercially available and DIY mounting systems and is the standard for most camera mounting gear. This threaded connection is compatible with the Magic Arm, RAM, and Loc-Line mounting systems.

The LipSync Joystick also has a rotatable mounting connection, so the threaded connection and interface cable can be directed in whichever way works best for the user. The “Up” position of the joystick should be rotated so that it matches the “Up” direction of the host device. Once mounted, the mounting angle of the LipSync Joystick can be adjusted by loosening the Outer Locking Ring, rotating the Front Section, and retightening the Outer Locking Ring.

Once a suitable mounting solution is selected, the following are the general steps to mount the LipSync Joystick:

1. Attach the LipSync Joystick to the end of
your mounting arm using the ¼-20 threads
and any necessary adapters.
2. Move your mounting arm to position the joystick as desired. The orientation of the Joystick in this step does not matter except that the overall device is positioned as the user prefers.

## USER GUIDE


Files available at www.github.com/makersmakingchange/LipSync | Page 9 of 51
3. Keeping the LipSync Joystick mounted in place, unscrew the Outer Locking Ring of the joystick by up to half a turn, or until the front section of the joystick can rotate freely against the fixed and mounted rear section.
4. Turn the front section of the joystick so that the Power Indicator LED points directly upwards.
5. Holding the front section in place, tighten the outer locking ring again until the front section is locked in place.

Note: This step will require two hands.

## USER GUIDE


Files available at www.github.com/makersmakingchange/LipSync | Page 10 of 51

### 2. Mount the LipSync Hub

The LipSync Hub should be mounted or placed in a location within view of the user. Ideally the LipSync Hub is located within 1 m of the user, near the host device screen. Like the Joystick, the LipSync Hub has a female ¼”-20 UNC threaded mounting connection on the back side of the device.

Using a mounting arm
1. Position your mounting arm so it does not interfere with your view of the screen so that the ¼-20 threaded end sits where you want to mount the Hub.
2. Connect the Hub to the Mounting Arm using the ¼-20 threads.
3. Adjust your mounting arm as needed to position the Hub specifically where you want it to be.

Mounted on a desk or table
1. Clear a space for the Hub to sit on the desk near the monitor. The Hub can rest on the back surface or can be connected to an optional desktop stand.
2. If using, mount the Hub in the stand with a ¼-20 bolt.
3. Place the Hub in the cleared off spot.

## USER GUIDE


Files available at www.github.com/makersmakingchange/LipSync | Page 11 of 51

### 3. Connect the LipSync Joystick to the LipSync Hub

The LipSync Joystick must be connected to the LipSync Hub using the LipSync Interface Cable. Attach one end of the cable to the Hub Port on the LipSync Joystick. Attach the other end of the cable to the Joystick Port on the LipSync Hub, which is labelled “JOY”. Ensure the cable is routed and secured appropriately to keep it from getting snagged or damaged.

Ensure you plug in the LipSync Interface Cable in the correct orientation. The tab side of the plug inserts into the narrower side of the outlet.

If the cable is damaged or a different length is required, the LipSync Interface Cable is a 4 conductor RJ11 phone cable.

## USER GUIDE


Files available at www.github.com/makersmakingchange/LipSync | Page 12 of 51

### 4. Optional: Connect Assistive Switches to the LipSync Hub

The LipSync Hub has three 3.5 mm ports for connecting external assistive switches. The three ports are labelled S1, S2, and S3. You can plug a switch into any combination of, or all the assistive switch ports as needed.

By default, an assistive switch attached to S1 will do puff inputs and an assistive switch attached to S3 will do sip inputs. These inputs can be used as an alternative input method if a user is unable to use sip or puff inputs effectively through the mouthpiece. A full summary of the Assistive Switch mapping is available in the Assistive Switch Inputs section.

After completing these steps, the LipSync is now ready to connect to the Host Device which is outlined in the next section.

## Connecting the LipSync Hub to the Host Device

The Host Device is the computer, tablet, laptop, smartphone, or other device that the user wants to control with the LipSync. How the LipSync is connected will depend on the type of Host Device and whether the LipSync is intended to operate as a USB Mouse, USB Gamepad, or Wireless Bluetooth Mouse.

The LipSync requires both a communication connection and a power connection.

To connect to the Host Device, you must first ensure that the device is powered, then check what mode it is in and change through the menu if required.

## USER GUIDE


Files available at www.github.com/makersmakingchange/LipSync | Page 13 of 51

### Powering the Device

The LipSync requires an external power source. Users can draw power from the host device (except on iOS devices) or use a USB power bank via the USB port on the Hub. The LipSync is provided with a USB-C to USB-A cable. Depending on the host device and operating mode, a suitable adapter or USB-C to a specific USB plug type cable may be required.

The general set-up will look like the following for any operating mode, where the required connection or adapter will vary depending on how you want to connect the device. When in Wireless mode, the LipSync can be connected directly to any power source.

See the below table for compatible power connection types for common host devices.

Common Host Devices | Power Connections | Common Cables for Direct Connection to Host Device | Common Adapters for Splitting to External Power
Direct to Host Device | Using External Power Source
Windows PC | USB-C to USB-C | Male USB 2 to Dual Female (https://www.amazon.ca/Female-Splitter-Power-Extension-Adapter/dp/B07CKQSTCB?hvadid=578878818136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)
| USB-A to USB-C | USB 2 Splitter (https://www.amazon.ca/Female-Splitter-Power-Extension-Adapter/dp/B07CKQSTCB?hvadid=578878818136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)
Mac | USB-C to USB-C | USB-C Splitter (https://www.amazon.ca/Adapter-Charging-Compatible-Samsung-Galaxy/dp/B09CTSHZR7?hvadid=579290833365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)
Android Phone/Tablet | USB-C to USB-C | USB-C Splitter (https://www.amazon.ca/Adapter-Charging-Compatible-Samsung-Galaxy/dp/B09CTSHZR7?hvadid=579290833365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)
| USB-C to USB-B Micro | Male USB-B Micro to Dual Female USB 2 Splitter (https://www.amazon.ca/dp/B06WPBSWHB?s=electronics&sp_csd=d2lkZ2V0TmFtZT1zcF9kZXRhaWw)
Apple Phone/Tablet | USB-C to Lightning | Lightning to USB 3 Adapter (https://www.apple.com/ca/shop/product/MK0W2AM/A/lightning-to-usb-3-camera-adapter)
| USB-C to USB-C | USB-C Splitter (https://www.amazon.ca/Adapter-Charging-Compatible-Samsung-Galaxy/dp/B09CTSHZR7?hvadid=579290833365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)

## USER GUIDE

Files available at www.github.com/makersmakingchange/LipSync | Page 14 of 51

More detailed instructions for how to connect the LipSync to various host devices in different modes are found below.

Once the LipSync is connected to power, it will turn on automatically. The Hub will emit a start-up tone and the Hub Display will show the current code version and the current operating mode. The Joystick must be plugged into the Hub for the device to fully power on.

### Changing the Operating Mode

The LipSync can operate in three modes: USB Mouse, Wireless Bluetooth Mouse, and USB Gamepad. The current operating mode is indicated on the display on startup and by the color of the Operating Mode Indicator. The default operating mode is USB Mouse.

Operating Mode | Operating Mode Indicator
USB Mouse | Purple
Wireless Mouse | Blue (Solid = connected, flashing = searching)
USB Gamepad | Yellow

The operating mode can be changed using the Hub Menu. For an explanation on how to perform the given inputs, see the section How to Perform LipSync Inputs.

Activating and navigating the Hub menu can be done using Sip and Puff, Hub Buttons or Assistive Switches according to the following table:
Output | Input
Sip / Puff | Assistive Switch | Hub Buttons
Enter/Exit menu | Puff – very long (>3 seconds) | S1 very long press (>3 seconds) | Select very long press (>3 seconds)
Enter/Exit Menu | N/A | Simultaneous Press of S1 and S3 | Simultaneous Press of Next and Sel
“Next” – goes to next option | Sip | S3 | Next
“Select” – Selects the current option | Puff | S1 | Sel

## USER GUIDE


Files available at www.github.com/makersmakingchange/LipSync | Page 15 of 51

### Connecting in USB Mouse Mode

Using the Hub Menu, ensure you are in USB Mouse mode. This is the default setting when the device is first programmed. When in USB Mouse mode, the operating mode indicator will turn purple.

Plugging Direct into a Computer or Laptop
If you have the appropriate cable, the LipSync can be directly plugged into the device’s USB port to work in USB Mouse or Gamepad mode. The Hub port requires a USB-C plug, and most host devices will require either USB-A or USB-C plug types.

The order in which you connect the USB cables may affect how the LipSync works. Connect the cables in the following order:

1. Connect the LipSync Interface Cable to the LipSync Joystick and LipSync Hub.
2. Connect a cable with a USB-C connection to the LipSync Hub, and the other end (either USB-C or USB-A) to the host device.
3. Wait 3 seconds for the LipSync to initialize. Initialization is complete when the Hub Display reads “Ready for use”.

Plugging Direct into an Android Mobile Device
The LipSync can be directly plugged into the device’s USB port to work in USB Mouse or Gamepad mode using the appropriate cable and/or adapter. The Hub port requires a USB C plug, and most host devices will require either USB-C, USB-B Micro, or USB-A plug types.
1. Connect the LipSync Interface Cable to the LipSync Joystick and LipSync Hub.
2. Connect a cable with a USB-C connection to the LipSync Hub, and the other end (depending on the device) to the host device.
3. Wait 3 seconds for the LipSync to initialize. Initialization is complete when the Hub Display reads “Ready for use”.

## USER GUIDE


Files available at www.github.com/makersmakingchange/LipSync | Page 16 of 51

Plugging into an iOS or Android Mobile Device with an External Power Source
The LipSync cannot draw power from an iOS device, and therefore must have a powered USB hub or powered USB splitter to connect between the LipSync Hub and iOS device. For an Android mobile device (phone or tablet), using an external power source is optional, but can extend the battery life of your device.

The order in which you connect the USB cables may affect how the LipSync works. Connect the cables in the following order if using an external power source:

1. Connect the LipSync Interface Cable to the LipSync Joystick and LipSync Hub.
2. Connect a USB-C cable to the LipSync Hub, and plug the other end into a USB Splitter or Powered Adapter. Connect the USB Splitter to power with the required cable.
3. Connect the other end of the splitter/adapter into the host device (USB-C or USB-B micro).
4. Wait 3 seconds for the LipSync to initialize. Initialization is complete when the Hub Display reads “Ready for use”.

Note that to use the LipSync with an iOS device, the device must have AssistiveTouch within the Accessibility Settings turned on. Instructions for how to set this up are in the Setting Up Host Device section.

## USER GUIDE


Files available at www.github.com/makersmakingchange/LipSync | Page 17 of 51

### Connecting in Wireless Mouse Mode

Using the LipSync as a Wireless Bluetooth Mouse requires a Bluetooth-compatible Host Device and an external power source. In Wireless Mouse Mode, the LipSync can be paired by a different host device, a USB Power Bank, or a USB wall power adapter.

The LipSync will need to be initially paired with the Host Device using the Host Device interface, which will likely require additional assistance. Once the LipSync is paired to a Host Device, it will automatically reconnect if the power is turned off and on again.

Use the following steps to connect in Wireless Mouse Mode:

1. Connect the LipSync Interface Cable to the LipSync Joystick and LipSync Hub.
2. Connect the LipSync Hub to a power source through the USB-C cable.
3. Wait 3 seconds for the LipSync to initialize. Initialization is complete when the Hub Display screen reads “Ready for use”.
4. If necessary, activate the Hub Menu and change the operating mode to BT Mouse mode.

Pairing the LipSync to a Bluetooth-Compatible Host Device
When the LipSync is in Wireless Mouse mode, it will automatically advertise itself as “LS_<Device-ID>”. The Device-ID is a sequence of 8 alphanumeric characters that are specific to each LipSync. You can determine the Device ID of your LipSync in the Info Menu. The Operating Mode Indicator on the Hub will flash blue indicating it is ready to pair.

On the host device:
1. Confirm that Bluetooth is activated.
2. Navigate to Settings > Bluetooth
3. Tap on LS_<Device-ID> to pair (where <device-ID> is a set of characters unique to each LipSync).
4. A Connected message will show beside the device name when it successfully connects.

Once paired, the indicator will remain a solid blue.

Note that when pairing with an iOS device, the device must have AssistiveTouch within the Accessibility Settings turned on to use the paired LipSync. Instructions for this are in the Setting Up Host Device Section.

## USER GUIDE

Files available at www.github.com/makersmakingchange/LipSync | Page 18 of 51

Reconnecting the LipSync to a Bluetooth-Compatible Host Device
If the LipSync is powered off, it will automatically reconnect to the previously paired Bluetooth Host Device when the LipSync is powered on again.

Disconnecting the LipSync from a Bluetooth-Compatible Host Device
If you no longer wish to use the LipSync with a particular device, you will need to disconnect the LipSync using the Bluetooth settings on the Bluetooth Compatible Host Device.

## USER GUIDE


Files available at www.github.com/makersmakingchange/LipSync | Page 19 of 51

### Connecting in USB Gamepad Mode

Gamepad mode is available through USB connection only and is compatible with any device that supports USB-HID connection. The LipSync Hub can be connected directly to a Computer, Laptop, or Android device in the same way as in USB Mouse Mode.

Using the menus through the Hub Display, ensure you are in Gamepad mode. USB Mouse mode is the default setting when the device is first programmed. When in Gamepad mode, the operating mode indicator will turn yellow.

When connecting to the Xbox Adaptive Controller (XAC), the XAC must be connected and paired with a device for the LipSync to receive power and function. The LipSync Hub can be plugged into either the left or right USB Joystick inputs. The following table links to resources for using the XAC and configuring controllers in Steam, a gaming platform.

QR Code | Resource

Adaptors for XAC compatibility with other systems. (https://www.makersmakingchange.com/s/managed-content-news/assistive-technology-in-gaming-MCTUYK7YHG6NFNTHPTBE7U5J4RTM)

Guide for remapping LipSync inputs with the XAC. (https://www.youtube.com/watch?v=gm4w4qXaDm8)

Guide for configuring a controller in Steam. (https://partner.steamgames.com/doc/features/steam_controller/getting_started_for_players)

## USER GUIDE

Files available at www.github.com/makersmakingchange/LipSync | Page 20 of 51

## Setting Up Host Device

There may be settings on the host device that enable the LipSync to be used more easily and/or more effectively.

Enable On-Screen Controls – Enables access to functions that usually require physical access to the device.

Enable On-Screen Keyboard – Provide a keyboard for inputting characters.

Adjust Host Device Cursor Size – Increasing cursor size can make it easier to see.

Adjust Host Device Cursor Speed – The cursor speed is adjustable on some devices. The cursor speed can also be adjusted separately on the LipSync.

Adjust Host Device Double Click Speed – Increasing the allowable delay between clicks may make it easier to input a double click.

### Enable On-Screen Controls

The assistant menu is a floating onscreen menu that allows access to important functions that cannot be accessed without physically touching the device, like the home button, back, zoom in and out, screen capture, volume, and restart.

On Android devices, turn on the Assistant Menu/ Accessibility Menu by going to Setting → Accessibility → Dexterity and Interaction → Assistant Menu

On iOS devices, turn on AssistiveTouch by going to Settings → Accessibility → Touch → AssistiveTouch

## USER GUIDE


Files available at www.github.com/makersmakingchange/LipSync | Page 21 of 51

On some devices, a swiping action is required to unlock it. This can be avoided by turning off screen lock. Alternatively, applications such as Keep Screen On can be downloaded from the Android Play store to prevent the phone from going to sleep. However, this will drain your phone battery faster.

QR Code | Resource
iPhone accessibility features. (https://support.apple.com/en-ca/guide/iphone/iph3e2e4367/ios)

Android accessibility features. (https://www.android.com/intl/en_ca/accessibility/)

Windows accessibility features. (https://support.microsoft.com/en-us/windows/discover-windows-accessibility-features-8b1068e6-d3b8-4ba8-b027-133dd8911df9)

Mac accessibility features. (https://support.apple.com/en-ca/guide/mac-help/mh35884/mac)

Android device | iOS device

## USER GUIDE

Files available at www.github.com/makersmakingchange/LipSync | Page 22 of 51

## Operating the LipSync

The LipSync has a range of inputs including the mouthpiece, optional assistive switches, and the buttons on the Hub. Using these inputs, the user, or support person, can adjust settings, change modes, and access the various output actions available in each mode.

### How to Perform LipSync Inputs

The LipSync has a range of inputs available through the mouthpiece, assistive switches, and Hub buttons. This section outlines how to perform each input type.

Moving The Joystick
To use the joystick, move the mouthpiece in the desired direction. You can hold the mouthpiece lightly in your mouth or lips, or between your lower lip and chin. The further the mouthpiece is moved, the faster the cursor will move. When the mouthpiece is released, it will return to its resting position.

Using Sip and Puff
Sip and puffs are the two forms of input available through the LipSync mouthpiece.

Sip
To perform a Sip Input, close your lips around the end of the mouthpiece and sip like you would a drink through a straw (i.e., inhale or apply negative pressure) and then release.

Puff
To perform a Puff Input, close your lips around the opening on the mouthpiece and blow air into it (i.e., exhale or apply positive pressure) and then release.

Using External Assistive Switches
Up to three External Assistive Switches with standard 3.5 mm audio jack plugs can be used with the LipSync to provide input. The Assistive Switches are connected to the LipSync Hub via the external switch ports labeled S1, S2, and S3.

By default, S1 and S3 are mapped to Puff and Sip to provide an alternate way to access those inputs for users who are unable to perform a puff and/or sip. S2 is not required but can provide access to an additional set of inputs.

Using the Hub Buttons
The Hub Buttons provide two functions: they provide a way to navigate the Hub Menu and they enable a support person to perform the same actions as sips and puffs without having to use the LipSync mouthpiece or the user’s assistive switches.

To activate the Hub Buttons, simply press down and then release on one or both of the round buttons on the face of the Hub. Next and Select (Sel) are both mapped to Sip and Puff, respectively.

## USER GUIDE

Files available at www.github.com/makersmakingchange/LipSync | Page 23 of 51

Timed Inputs
The amount of time that any input (Sip/puff/switches/buttons) is held before being released will trigger different actions.

Short: Less than 1 second. Indicated by the respective LED blinking once.
Long: Between 1 to 3 seconds. Indicated by the respective LED lighting up and staying on.
Very Long: 3 seconds or longer. Indicated by the respective LED turning back off.

For each input in regular operating modes, a specified Feedback Light will indicate the input duration. The feedback lights are designated to the inputs as follows:

Left Light •: Puff, S1, Select (Sel) button on Hub
Middle Light ••: S2
Right Light •••: Sip, S3, Next button on Hub

For example, to perform a Very Long Sip, close your lips around the end of the mouthpiece and apply a sip to the tube. After you hold the Sip for 1 second, the Right Feedback Light on the Hub will turn on. After 3 seconds, the Right Feedback Light will turn off. Release the pressure to trigger a Very Long Sip.

### USB & Wireless Mouse Mode

In either USB or Wireless Mouse Mode, the joystick controls the cursor, and the sip and puff are mapped to different mouse button clicks.

Mouse Mode Functions
Function | Description
Moving the Cursor | Performs the same function as moving a mouse to move the pointer/cursor on the screen.
Left Click | Performs the same function of the left click on a mouse
Right Click | Performs the same function of the right click on a mouse
Middle Click | Performs the same function of the scroll wheel push on a mouse
Drag Mode | Will mimic the left click on the mouse held down to drag items on the screen such as folders
Scroll Mode | Keeps the mouse stationary and the joystick can control the scroll speed

Moving the Cursor
To move the cursor, move the mouthpiece in the desired direction. You can hold the mouthpiece lightly in your mouth or lips, or between your lower lip and chin. The further the mouthpiece is moved, the faster the cursor will move. Releasing the mouthpiece will return it to the center position and the cursor will stop moving.

If the cursor continues to move after the mouthpiece is released see the Troubleshooting Section: page 42.

## USER GUIDE

Files available at www.github.com/makersmakingchange/LipSync | Page 24 of 51

The maximum cursor speed can be adjusted by the user in the Hub Menu. See the Changing the Cursor Speed section.

Left Clicking
To do a left click, use your mouth to do a short puff on the mouthpiece (i.e., exhale or apply positive pressure). The left click will be generated when the short puff is released, and the left LED will blink once.

A left click can also be generated by a short press of the Hub “Select” button or S1.

Right Clicking
To do a right click, use your mouth to do a short Sip (<1 second) on the mouthpiece (i.e., inhale or apply negative pressure). The right click will be generated when the short sip is released, and the right LED will blink once.

A right click can also be generated by a short press of the Hub “Next” button or S3.

Double Clicking
To do a double click, use your mouth to do two short puffs on the mouthpiece. The left LED will blink once for each puff.

It may be helpful to decrease the double click speed on the host device.

Middle Clicking
Middle click is used for tasks such as turning the cursor into scroll mode in web browsers and in documents. On a typical mouse, a middle click is accomplished by clicking the scroll wheel. Note that not all mice have a scroll wheel that clicks.

To do a middle click, apply and maintain a very long sip (At least 3 seconds) to the mouthpiece and then then release the sip. The right-side LED will begin flashing quickly once the duration has been reached.

A middle click can also be generated by a very long press of S3 or the Hub “Next” button, or a short press of S2.

Drag
Drag is used for tasks such as repositioning windows or icons, or selecting objects such as text. On a typical mouse, drag is accomplished by pressing and holding the left click. On the LipSync, drag is accomplished by starting Drag mode.

To start Drag Mode, apply and maintain a long puff (between 1 and 3 seconds) on the mouthpiece and then release the puff. The Left Feedback Light will turn on and stay on once the duration has been reached. Alternative inputs are a long press of the Hub “Select” button, or a long press of S1.

To drag, move the mouthpiece in any direction.

## USER GUIDE

Files available at www.github.com/makersmakingchange/LipSync | Page 25 of 51

To stop drag mode, apply a short sip or a short puff on the mouthpiece.

Vertical Scroll
Vertica scroll is useful for scrolling up and down within documents or webpages. On a typical mouse, this is often controlled by rotating a scroll wheel. On the LipSync, vertical scrolling is accomplished by activating Scroll Mode and using vertical motion of the mouthpiece.

To start Scroll Mode, input a Long Sip (1 and 3 seconds). The Right Feedback Light will turn on when the Long Sip threshold has been reached. Alternative inputs are a long press of the Hub “Next” button, or a long press of S3. The right Feedback Light will remain on while Scroll Mode is active.

To scroll, move the mouthpiece up or down. The further the mouthpiece is moved, the faster the scroll.

To stop scroll mode, apply a short sip or a short puff on the mouthpiece.

The scroll speed can be adjusted by the user using the Hub Menu. See the Changing the Scroll Speed section.

### USB Gamepad Mode

In Gamepad mode, the LipSync inputs are translated to gaming outputs instead of mouse functions. The LipSync will act as a gamepad with one joystick and 6 buttons.

In some direct applications, these buttons will have default functions, such as when plugged into the XAC, or plugged into a mobile smart phone. When used with a program such as Steam, the inputs will have to be mapped to the desired outputs to setup the LipSync as a controller. Note that while the LipSync inputs are set to default outputs with the XAC, you can modify this mapping through the Xbox Accessories App. (https://support.xbox.com/en-CA/help/account-profile/accessibility/customize-adaptive-controller-in-xbox-accessories-app)

Gamepad Mode Functions
Function | Description
Moving the Joystick | Performs the same function as moving a standard joystick or thumbstick in gaming applications.
Button 1 Press | Performs the same function of pressing button 1 on a standard gamepad.
Button 2 Press | Performs the same function of pressing button 2 on a standard gamepad.
Button 3 Press | Performs the same function of pressing button 3 on a standard gamepad.
Button 4 Press | Performs the same function of pressing button 4 on a standard gamepad.
Button 5 Press | Performs the same function of pressing button 5 on a standard gamepad.
Button 6 Press | Performs the same function of pressing button 6 on a standard gamepad.

Moving the Joystick
To move the joystick, move the mouthpiece in the desired direction. You can hold the mouthpiece lightly in your mouth or lips, or between your lower lip and chin. The further the mouthpiece is moved,

## USER GUIDE

Files available at www.github.com/makersmakingchange/LipSync | Page 26 of 51

the further the joystick will move. Releasing the mouthpiece will return it to the center position and the joystick will return to center.

If the cursor continues to move after the mouthpiece is released see the Troubleshooting Section: page 42.

Button 1 Press
To do a button 1 press, use your mouth to do a short puff on the mouthpiece (i.e., exhale or apply positive pressure). The button 1 press will be generated when the short puff is released.

A button 1 press can also be generated by a short press of the Hub “Select” button or S1.

Button 2 Press
To do a button 2 press, use your mouth to do a short Sip (<1 second) on the mouthpiece (i.e., inhale or apply negative pressure). The button 2 press will be generated when the short sip is released.

A button 2 press can also be generated by a short press of the Hub “Next” button or S3.

Button 3 Press
To do a button 3 press, apply and maintain a long puff (between 1 and 3 seconds) on the mouthpiece and then release the puff. The button 3 press will be generated when the long puff is released.

A button 3 press can also be generated by a long press of the Hub “Select” button or S1.

Button 4 Press
To do a button 4 press, apply and maintain a long sip (between 1 and 3 seconds) on the mouthpiece and then release the sip. The button 4 press will be generated when the long sip is released.

A button 4 press can also be generated by a long press of the Hub “Next” button or S3.

Button 5 Press
To do a button 5 press, apply and maintain a very long sip (between 1 and 3 seconds) on the mouthpiece and then release the sip. The button 5 press will be generated when the very long sip is released.

A button 5 press can also be generated by a very long press of the Hub “Next” button, or a short press of S2.

Button 6 Press
To do a button 6 press, perform a long press (between 1 to 3 seconds) of S2. The button 6 press will be generated when the long press of S2 is released.

USB Gamepad Mode connected to an Android Smart Phone or Tablet
When connected to a smart phone in Gamepad Mode, the LipSync acts similar to switch scanning, but uses the joystick to move the scanning target.

## USER GUIDE

Files available at www.github.com/makersmakingchange/LipSync | Page 27 of 51
Function | Description
Moving the Scanning Target | Moves the target selector around the screen one target at a time, side to side, or up and down.
Select | Performs the same function as tapping on the selected field.
Back | Performs the same function as the back button on an Android smart phone.

Moving the Scanning Target
To move the scanning target, move the joystick in one of the four cardinal directions: up, down, left, or right. If the joystick is held in the chosen direction, the selection field will move in that direction, highlighting the different apps or selections as it goes.

Select
To select the highlighted field, use your mouth to do a short puff on the mouthpiece (i.e., exhale or apply positive pressure). The Select function will be performed when the short puff is released.

The Select function can also be generated by a short press of the Hub “Select” button or S1.

Back
To use the Back function, use your mouth to do a short Sip (<1 second) on the mouthpiece (i.e., inhale or apply negative pressure). The Back function will be performed when the short sip is released.

A Back function can also be performed by a short press of the Hub “Next” button or S3.

### Input and Feedback Summary

The overall mapping of the LipSync inputs and feedback features is as follows:

Feedback Features
Each Feedback Light is designated to a set of inputs:

Left Light •: Puff, S1
Middle Light ••: S2
Right Light •••: Sip, S3

The time durations Short, Long, and Very Long for the Sip/Puff and switch/button inputs are the following:

Short: Less than 1 second. Feedback Light blinks once when released.
Long: Between 1 to 3 seconds. Feedback Light turns on and stays on.
Very Long: 3 seconds or longer. Feedback Light turns back off.

## USER GUIDE

Files available at www.github.com/makersmakingchange/LipSync | Page 28 of 51

Mouthpiece Inputs
LipSync Mouthpiece Inputs | Hub Menu | Mouse (PC or Mobile) | Gamepad
PC | Mobile (Android) | XAC (Left USB) | XAC (Right USB)
Joystick | Can move joystick to test cursor speeds and view on screen | Cursor movement | Joystick movement | Directional pad | Left Thumbstick | Right Thumbstick
Short Puff | Select | Left click | Button 1 | Select | X1 (Left Stick Up) | View
Long Puff | N/A | Start Drag Mode | Button 3 | Select | Left Stick Press | Right Stick Press
Very Long Puff | Exit Hub Menu | Enter Hub Menu | Enter Hub Menu | Enter Hub Menu | Enter Hub Menu | Enter Hub Menu
Short Sip | Next | Right click | Button 2 | Back | X2 (Left Stick Down) | Menu
Long Sip | N/A | Start Scroll Mode | Button 4 | N/A | Left Bumper | Right Bumper
Very Long Sip | N/A | Middle Click | Button 5 | Select | A | X

Assistive Switch Inputs
LipSync Assistive Switch Inputs | Hub Menu | Mouse (PC or Mobile) | Gamepad
PC | Mobile (Android) | XAC (Left USB) | XAC (Right USB)
S1 Short Press | Select | Left Click | Button 1 | Select | X1 (Left Stick Up) | View
S1 Long Press | N/A | Start Drag Mode | Button 3 | Select | Left Stick Press | Right Stick Press
S1 Very Long Press | Exit Hub Menu | Enter Hub Menu | Enter Hub Menu | Enter Hub Menu | Enter Hub Menu | Enter Hub Menu
S2 Short Press | N/A | Middle Click | Button 5 | Back | A | X
S2 Long Press | N/A | N/A | Button 6 | N/A | B | Y
S2 Very Long Press | N/A | Perform Center Reset | Perform Center Reset | Perform Center Reset | Perform Center Reset | Perform Center Reset

## USER GUIDE

Files available at www.github.com/makersmakingchange/LipSync | Page 29 of 51
LipSync Assistive Switch Inputs | Hub Menu | Mouse (PC or Mobile) | Gamepad
PC | Mobile (Android) | XAC (Left USB) | XAC (Right USB)
S3 Short Press | Next | Right Click | Button 2 | Select | X2 (Left Stick Down) | Menu
S3 Long Press | N/A | Start Scroll Mode | Button 4 | N/A | Left Bumper | Right Bumper
S3 Very Long Press | N/A | Middle Click | N/A | Select | N/A | N/A

Chorded Inputs (Simultaneous short press)
S1 and S3 | Exit Hub Menu | Enter Hub Menu

Enter Hub
Menu

Enter Hub
Menu

Enter Hub
Menu

Enter Hub
Menu

Hub Button Inputs
LipSync Hub Button Inputs | Hub Menu | Mouse (PC or Mobile) | Gamepad
PC | Mobile (Android) | XAC (Left USB) | XAC (Right USB)
Select Short Press | Select | Left Click | Button 1 | Select | X1 (Left Stick Up) | View
Select Long Press | N/A | Start Drag Mode | Button 3 | Select | Left Stick Press | Right Stick Press
Select Very Long Press | Exit Hub Menu | Enter Hub Menu | Enter Hub Menu | Enter Hub Menu | Enter Hub Menu | Enter Hub Menu
Next Short Press | Next | Right Click | Button 2 | Back | X2 (Left Stick Down) | Menu
Next Long Press | N/A | Start Scroll Mode | Button 4 | N/A | Left Bumper | Right Bumper
Next Very Long Press | N/A | Middle Click | Button 5 | Select | A | X

Chorded Inputs (Simultaneous short press)

### Next and Select

Exit Hub Menu Enter Hub Menu

Enter Hub
Menu

Enter Hub
Menu

Enter Hub
Menu

Enter Hub
Menu
Note: Default XAC mappings can be modified through the Xbox Accessories App. (https://support.xbox.com/en-CA/help/account-profile/accessibility/customize-adaptive-controller-in-xbox-accessories-app)

## USER GUIDE

Files available at www.github.com/makersmakingchange/LipSync | Page 30 of 51

## The Hub Menu

The Hub is an interface device used to connect the LipSync joystick and assistive switches to the Host Device. The Hub also contains a display that shows the Hub Menu, an interface for adjusting settings, calibrating the joystick, changing the operating mode, restarting the device, and resetting to the default settings.

### Accessing the Hub Menu

The Hub Menu is normally off to reduce power consumption and wear on the screen. To use the Hub Menu, it must first be activated using sip and puff, assistive switches, or the Hub Buttons. The following table shows the corresponding input options to enter/exit the Hub Menu.

Action | Input
On Hub Button | Assistive Switch | Sip / puff
Enter/Exit menu | Select very long press (>3 seconds) | S1 very long press (>3 seconds) | Puff – very long (>3 seconds)
Enter/Exit Menu | Simultaneous Press of Next and Sel | Simultaneous Press of S1 and S3 | N/A

### Navigating the Hub Menu

Once the Hub Menu is activated, it will display a list of menus. The current selection will be indicated by a left arrow (>). The Hub Menu is navigated using inputs from sip and puff, assistive switches, and/or the Hub Buttons. The following table shows the corresponding input options to navigate the Hub Menu.

Action | Input
On Hub Button | Assistive Switch | Sip / puff
“Next” – goes to next option | Next | S3 | Sip
“Select” – Selects the pointed to option | Sel | S1 | Puff

When “Next” is activated, the selection will change to the next item on the list. If “Next” is activated when the selection is on the last item of the list, the selection will change to the top item on the list. A “Next” action is trigged using a Sip, a short press on S3, or by pressing the Next button on the Hub.

When “Select” is activated, the current selection will be activated, such as opening a submenu, starting calibration, etc. The “Select” action is trigged using a Puff, a short press on S1, or by pressing the Select button on the Hub.

## USER GUIDE

Files available at www.github.com/makersmakingchange/LipSync | Page 31 of 51

### Hub Menu Options

The Hub Menu is arranged as sets of submenus and pages. Each submenu has a “… Back” option at the end of its list to return to the top of the previous menu. Any selection made will walk you through the required steps with instructions on the Hub Display. The overall structure of the Hub Menu is as follows:

> Exit Menu
> Center Reset
> Mode
> Mouse USB
> Mouse BT
> Gamepad
> Cursor speed
> More
> Sound
> Light Brightness
> Scroll Speed
> Sip & Puff
> Sip threshold
> Puff threshold
> Full Calibration
> Restart LipSync
> Factory Reset
> Info

Exit Menu
The top menu item is to exit and deactivate the Hub Menu. After performing any other setting changes, or backing out of submenus, the menu display will always return to the top of the main menu, so it is easy to exit the menu after changing settings. When selected, you will be asked to confirm you wish to leave the menu and can select “Confirm” to exit, or “… Back” to return to the menu.

As shown in the table for navigating the menus, any function used to enter the menu, can also be used to exit it.

Center Reset
A center reset will reset the neutral resting position of your joystick and should be used if you are experiencing drift. Do not touch the joystick while performing a center reset.

## USER GUIDE

Files available at www.github.com/makersmakingchange/LipSync | Page 32 of 51

Mode
The Mode submenu allows you to change the operating mode by selecting one of three modes: USB Mouse, BT Mouse, or Gamepad. Note that it is important to ensure you are in the correct mode for the device you want to connect to. After changing modes, the Hub will reset and perform a center reset upon powering on. Do not touch the joystick until you see the Hub display read “Ready for use” and the mode.

Cursor Speed
The Cursor Speed submenu allows you to increase or decrease the mouse cursor speed in increments of 1 from a scale of 1 to 10. While changing the increment, the cursor can still be moved across the screen to test the current speed setting.

More
The More submenu contains further Menu Items that generally will not be used as often.

Sound On/Off
This menu item will toggle the sound feedback for LipSync inputs on or off. There is no volume control.

Light Brightness
Thie menu allows you to increase or decrease the brightness of the lights on the Hub in increments of 1 from a scale of 0 to 10.

Scroll Speed
This menu allows you to increase or decrease the mouse scroll speed in increments of 1 from a scale of 1 to 10.

Sip & Puff
This menu allows you to adjust the sip and puff threshold to fine tune the required air pressure for sips and puff. The sip and puff thresholds can be set independently.

Full calibration
A full calibration is used to set the extents of your joystick and should be done if you are having issues moving in certain directions with the joystick.

Restart LipSync
This option provides a way for the user to reset the LipSync without physically disconnecting it from power.

Factory Reset
This option will trigger a factor reset that returns all settings back to default. This includes the operating mode, cursor speed, calibrations, and any settings adjusted through the API.

## USER GUIDE

Files available at www.github.com/makersmakingchange/LipSync | Page 33 of 51

Info
This option will display a page with information about the LipSync, including the current firmware version and the unique hardware ID that is used for the Bluetooth device name.

## USER GUIDE

Files available at www.github.com/makersmakingchange/LipSync | Page 34 of 51

## Adjusting the LipSync

Adjustments to the LipSync involve calibrating the joystick, and changing settings. To adjust the LipSync, most settings can be changed through the Hub Display menu.

### Center Reset

A Center Reset resets the neutral position of the joystick in its resting position. If the position of the cursor is moving when the mouthpiece is released and stationary, a Center Reset can help resolve the cursor drift.

A Center Reset should be performed in the following situations:

1. The LipSync mounting angle is adjusted.
2. The LipSync filter and/or mouthpiece is replaced.
3. The cursor continues to move when the mouthpiece is released and is stationary.

A Center Reset is automatically performed when the LipSync is first powered on, and at the end of the Full Calibration process. A Center Reset can also be started manually using the Hub Menu or outside of the menu using a Very Long Press on an Assistive Switch attached to S2:

### 1. Using the Hub Menu:

a. Activate the Hub Menu by applying a very long (>3 seconds) Puff (or Select Button or S1) on the mouthpiece and then release it.
i. An alternative way to open the Hub Menu is a simultaneous short press of S1 and S3, or Next and Select on the Hub.
b. The Hub Menu will turn on.
c. Use a short Puff input (Or Next button or S3) to move through the Menu options until you reach “Center Reset.”
d. Use a Short Sip (<1 seconds) input (Or Select Button or S1) to select “Center Reset.”
e. Use a Short Sip (<1 seconds) input (Or Select Button or S1) to select “Center Reset” again.
f. Release the joystick and do not touch it until the menu screen returns to the regular menu.
2. Using Long Press on Assistive Switch S2:
a. Perform a Very Long Press (>3 seconds) of S2.
b. Release the joystick and do not touch it until the Hub screen states that the center reset is complete.

When the Center Reset is started, the Hub Menu Display will prompt you to not touch the joystick. It is important to release the mouthpiece and leave it to sit in its neutral resting position to perform the center reset.

## USER GUIDE

Files available at www.github.com/makersmakingchange/LipSync | Page 35 of 51

### Full Calibration

The Full Calibration of the LipSync should be completed upon initial assembly of the device. It may also need to be repeated if the user is experiencing strange cursor movements or no change in movement at the extents of the joystick.

The calibration procedure is a timed process that required the joystick to be moved to each corner of the movement range. The Hub menu display will give prompts to follow for moving the joystick.

### 1. Initiate Full Calibration

a. Apply and maintain a very long (>3 seconds) Puff (or Select Button or S1) on the mouthpiece and then release it.
i. An alternative way to open the Hub Menu is a simultaneous short press of S1 and S3, or Next and Select on the Hub.
b. The Hub Menu will turn on.
c. Use a short Sip (<1 second) input (Or Next button or S3) to move through the Menu options until you reach “More”
d. Use a short Puff (<1 second) input (Or Sel Button or S1) to select “More”
e. Use a short Sip (<1 second) input (Or Next button or S3) to move through the menu options until you reach “Full Calibration.”
f. Use a short Puff (<1 second) input (Or Sel Button or S1) to select “Full Calibration”
g. On the screen reading “Are you sure?” use a short Puff (<1 second) input (Or Sel Button or S1) to select “Confirm.”
h. Release the joystick and follow the prompts on the Hub Menu Display.

### 2. Follow Full Calibration Prompts

a. The Hub Display will show “Follow on screen prompts”
b. The Hub will beep once, all lights will flash once, and the Display will show “Hold joystick top left”
i. Move the joystick/mouthpiece to the top left corner extent of the joystick and hold it there until the prompt changes, also signified by the Hub beeping once and all lights flashing once.
c. The Hub Display will show “Hold joystick top right”
i. Move the joystick/mouthpiece to the top right corner extent of the joystick and hold it there until the prompt changes, also signified by the Hub beeping once and all lights flashing once.
d. The Hub Display will show “Hold joystick bottom right”
i. Move the joystick/mouthpiece to the bottom right corner extent of the joystick and hold it there until the prompt changes, also signified by the Hub beeping once and all lights flashing once.
e. The Hub Display will show “Hold joystick bottom left”

## USER GUIDE

Files available at www.github.com/makersmakingchange/LipSync | Page 36 of 51
i. Move the joystick/mouthpiece to the bottom left corner extent of the joystick and hold it there until the prompt changes, also signified by the Hub beeping once and all lights flashing once.
f. The Hub Display will show “Release, do not move joystick”
i. Release the joystick back to its neutral position and do not touch it.

NOTE: during each step of the full calibration, if the joystick is not moved to one of the corners, and is left at rest in the center, the display will show the message “Movement too small. Returned to default.” Meaning that the default value for the corner of a typical joystick will be used, so that the calibration does not lead to undesired results.

### 3. Calibration Complete

a. When the calibration is complete, the Hub Display will show “Joystick Calibrated” and then return to the main menu screen.
b. You can test the joystick movement on the host device screen to ensure the calibration was successful.
c. You can now continue through the menu settings or exit the menu and use your joystick.

### Changing LipSync Settings

There are numerous settings that control the operation of the LipSync. Some of these settings can be adjusted independently through the Hub Menu.

Table 1: LipSync Settings
Setting | Default | Min | Max | Note
Cursor Speed | 5 | 0 | 10 | Changes the cursor speed in any Mouse Mode.
Sound Feedback | On | Off | On | Turns the sound on or off.
Light Brightness Level | 5 | 0 | 10 | Adjust the brightness of the LED lights. To turn off the lights completely, set to level 0.
Scroll Speed | 5 | 1 | 10 | Changes the scrolling speed in any Mouse Mode.
Sip Threshold | 3.0 | 1.0 | 100.0 | Changes the pressure required for a Sip input.
Puff Threshold | 3.0 | 1.0 | 100.0 | Changes the pressure required for a Puff input
Inner Deadzone | 0.05 | 0.0 | 0.5 | Changes the distance the joystick must be moved from rest to cause cursor/gamepad movement. Only adjustable through API, not Hub menu.
Outer Deadzone | 0.95 | 0.5 | 1.0 | Changes the distance the joystick must be moved from the outer edge to provide full cursor/gamepad movement. Only adjustable through API, not Hub menu.

## USER GUIDE

Files available at www.github.com/makersmakingchange/LipSync | Page 37 of 51

Changing the Cursor Speed
To change the cursor speed, the host device settings can be adjusted, or the LipSync cursor speed can be adjusted. To change the LipSync cursor speed:
1. Activate the menu using a very long Puff (>3 seconds) on the mouthpiece
a. Alternatively, the Hub Menu can be activated using a very long press on Select Button or S1; or by a simultaneous short press of S1 and S3, or Next and Select on the Hub.
2. Use a short Sip (<1 second) input (Or Next button or S3) to move through the Menu options until you reach “Cursor speed”
3. Use a short Puff (<1 second) input (Or Sel Button or S1) to select “Cursor speed”
4. Use a short Sip (<1 second) input (Or Next button or S3) to move through the Menu options “increase” and “decrease”
5. Use a short Puff (<1 second) input (Or Sel Button or S1) to select “increase” or “decrease” as desired.
a. Note: the minimum cursor speed level is 1, and the maximum is 10.
6. Test the cursor speed on the host device by moving the joystick while in the menu.
7. Once happy with the cursor speed, navigate to “…Back” using a short (<1 seconds) Sip input (Or Next button or S3).
8. Use a short Puff (<1 second) input (Or Sel Button or S1) to select “…Back”
9. Use a short Puff (<1 second) input (Or Sel Button or S1) to select “Exit Menu” or continue through the menu to adjust other settings.

Changing the Scroll Speed
The scroll speed controls how much the screen scrolls with vertical motion of the mouthpiece when Scroll Mode is activated. To change the LipSync scroll speed:
1. Activate the menu using a very long Puff (>3 seconds) on the mouthpiece
b. Alternatively, the Hub Menu can be activated using a very long press on Select Button or S1; or by a simultaneous short press of S1 and S3, or Next and Select on the Hub.
2. Use a short Sip (<1 second) input (Or Next button or S3) to move through the Menu options until you reach “More”
3. Use a short Puff (<1 second) input (Or Sel Button or S1) to select “More”
4. Use a short Sip (<1 second) input (Or Next button or S3) to move through the Menu options until you reach “Scroll speed”
5. Use a short Puff (<1 second) input (Or Sel Button or S1) to select “Scroll speed”
6. Use a short Sip (<1 second) input (Or Next button or S3) to move through the Menu options “increase” and “decrease”
7. Use a short Puff (<1 second) input (Or Sel Button or S1) to select “increase” or “decrease” as desired.
a. Note: the minimum scroll speed level is 1, and the maximum is 10.
8. Test the scroll speed on the host device by moving the joystick while in the menu.

## USER GUIDE

Files available at www.github.com/makersmakingchange/LipSync | Page 38 of 51
9. Once happy with the scroll speed, navigate to “…Back” using a short (<1 seconds) Sip input (Or Next button or S3).
10. Use a short Puff (<1 second) input (Or Sel Button or S1) to select “…Back”
11. Use a short Puff (<1 second) input (Or Sel Button or S1) to select “Exit Menu” or continue through the menu to adjust other settings.

Changing the Light Brightness
The brightness of the Hub lights can be adjusted to suit the user’s preference. A user may wish to increase the brightness when working in a bright environment or decrease the brightness when working in a dark room. The brightness of the lights can be adjusted from Level 0 (completely off) to Level 10 (full brightness). To change the brightness:
1. Activate the menu using a very long Puff (>3 seconds) on the mouthpiece
a. Alternatively, the Hub Menu can be activated using a very long press on Select Button or S1; or by a simultaneous short press of S1 and S3, or Next and Select on the Hub.
2. Use a short Sip (<1 second) input (Or Next button or S3) to move through the Menu options until you reach “More”
3. Use a short Puff (<1 second) input (Or Sel Button or S1) to select “More”
4. Use a short Sip (<1 second) input (Or Next button or S3) to move through the Menu options until you reach “Light Brightness”
5. Use a short Puff (<1 second) input (Or Sel Button or S1) to select “Light Brightness”
6. Use a short Sip (<1 second) input (Or Next button or S3) to move through the Menu options “increase” and “decrease”
7. Use a short Puff (<1 second) input (Or Sel Button or S1) to select “Increase” or “Decrease” as desired.
a. Note: the minimum brightness level is 0, and the maximum is 10.
8. The Hubs lights will briefly illuminate to preview the new brightness.
9. Once happy with the brightness, navigate to “…Back” using a short (<1 seconds) Sip input (Or Next button or S3).
10. Use a short Puff (<1 second) input (Or Sel Button or S1) to select “…Back”
11. Use a short Puff (<1 second) input (Or Sel Button or S1) to select “Exit Menu” or continue through the menu to adjust other settings.

Changing the Sound Mode
Sound feedback can be turned on or off. To change the LipSync Sound Mode:
1. Activate the menu using a very long Puff (>3 seconds) on the mouthpiece
a. Alternatively, the Hub Menu can be activated using a very long press on Select Button or S1; or by a simultaneous short press of S1 and S3, or Next and Select on the Hub.
2. Use a short Sip (<1 second) input (Or Next button or S3) to move through the Menu options until you reach “More”

## USER GUIDE

Files available at www.github.com/makersmakingchange/LipSync | Page 39 of 51
3. Use a short Puff (<1 second) input (Or Sel Button or S1) to select “More”
4. Use a short Sip (<1 second) input (Or Next button or S3) to move through the Menu options until you reach “Sound”
5. Use a short Puff (<1 second) input (Or Sel Button or S1) to select “Sound”
6. The current sound mode will be indicated (either ON or OFF).
7. Use a short Puff (<1 second) input (Or Sel Button or S1) to select “Turn off “ or “Turn on” to toggle the Sound Mode.
8. Once happy with the Sound Mode, navigate to “…Back” using a short (<1 seconds) Sip input (Or Next button or S3).
9. Use a short Puff (<1 second) input (Or Sel Button or S1) to select “…Back”
10. Use a short Puff (<1 second) input (Or Sel Button or S1) to select “Exit Menu” or continue through the menu to adjust other settings.

Changing the Sip & Puff Thresholds
The Sip and Puff thresholds can be individually changed to accommodate the user’s preferences. This changes how hard the user needs to Sip or Puff (i.e. the amount of pressure) for the input to be registered. Sip and Puff thresholds can be set from 1 to 100 hPa and are defaulted to 3 hPa. To change the sip or puff thresholds:
1. Activate the menu using a very long Puff (>3 seconds) on the mouthpiece (or Select Button or S1)
a. An alternative way to open the Hub Menu is a simultaneous short press of S1 and S3, or Next and Sel on the Hub.
2. The Hub Menu will turn on.
3. Use a short (<1 seconds) Sip input (Or Next button or S3) to move through the Menu options until you reach “More”
4. Use a short (<1 seconds) Puff input (Or Sel Button or S1) to select “More”
5. Use a short (<1 seconds) Sip input (Or Next button or S3) to move through the Menu options until you reach “Sip & Puff”
6. Use a short (<1 seconds) Puff input (Or Sel Button or S1) to select “Sip & Puff”
7. Use a short (<1 seconds) Sip input (Or Next button or S3) to move through the Menu options to select “Sip Threshold” or “Puff Threshold”
8. Use a short (<1 seconds) Puff input (Or Sel Button or S1) to select “Sip Threshold” or “Puff Threshold”
9. Use a short (<1 seconds) Sip input (Or Next button or S3) to move through the Menu options “increase” and “decrease”
10. Use a short (<1 seconds) Puff input (Or Sel Button or S1) to select “increase” or “decrease” as desired.
11. Once happy with the Sip or Puff Threshold, navigate to “…Back” using a short (<1 seconds) Sip input (Or Next button or S3).
12. Use a short (<1 seconds) Puff input (Or Sel Button or S1) to select “…Back”

## USER GUIDE

Files available at www.github.com/makersmakingchange/LipSync | Page 40 of 51
13. Use a short (<1 seconds) Puff input (Or Sel Button or S1) to select “Exit Menu” or continue through the menu to adjust other settings.

Input-Output Mapping
The mapping of inputs (e.g., Short Sip, Very Long Puff) to actions (e.g., Right Click, Activate Menu) are currently fixed in code and not adjustable by the user. Contact your maker or support for assistance.

Changing Settings Through the Serial Interface (API)
All the user-adjustable settings of the LipSync are accessible through the Serial Interface. This is a more challenging method intended only for advanced users. Refer to Appendix A: Serial Interface (Application Programming Interface) for more information.

## USER GUIDE


Files available at www.github.com/makersmakingchange/LipSync | Page 41 of 51

## Maintenance

This section outlines how to perform common maintenance tasks for the LipSync. The device should be kept clean of dust and debris as needed by following the cleaning instructions.

### Replacing the Mouthpiece

The filtered mouthpiece should be replaced as needed, or at least every 30 to 90 days under normal daily use. To replace the mouthpiece:

1. Remove the mouthpiece.
Hold the filter and rotate it counter-clockwise until it comes out of the gimbal connector.
2. Discard the mouthpiece assembly.
3. Install a new mouthpiece assembly.
Twist the filter clockwise until finger tight. Do not overtighten.

## USER GUIDE

Files available at www.github.com/makersmakingchange/LipSync | Page 42 of 51

### Cleaning the LipSync

Cleaning the LipSync Joystick
✓ | Wipe with a damp cloth
✗ | Don’t use abrasive cleaning materials
✗ | Don’t soak the LipSync Joystick in any cleaning
solutions
✗ Don’t immerse the LipSync Joystick

Cleaning the LipSync Hub
✓ | Wipe plastic enclosure with a damp cloth
✗ | Don’t scrub or press down on the Hub Display
✗ | Don’t use abrasive cleaning materials
✗ | Don’t soak the LipSync Hub in any cleaning
solutions
✗ Don’t immerse the LipSync Hub

## Frequently Asked Questions

Can the LipSync be used by multiple users?

- The LipSync Joystick is intended as a single user device. The Hub can be used for different joysticks, but the joystick itself should only be used by one person.

## Troubleshooting

Mouse cursor is not visible
- Make sure device is connected
- Make sure device is in the intended operating mode (e.g., USB, not Wireless)
- Make sure the device has proper onscreen settings (e.g., AssistiveTouch on iOS)

Mouse cursor is difficult to see
- Adjust the size or color of the cursor on the host device

Producing sips and puff required too much or too little air pressure
- Adjust the sip and puff threshold
- Change the mouthpiece

Cursor movement is too slow or too fast
- Adjust the cursor speed on the LipSync
- Adjust the cursor speed on the host device

Difficulty inputting a double-click
- Adjust host devices double click rate

Cursor / Joystick Drift

- Trigger a center reset
a. Activate the Hub Menu and navigate to Center reset.
b. Using a very long press of Assistive Switch 2
c. Disconnected and reconnect power.

## USER GUIDE

Files available at www.github.com/makersmakingchange/LipSync | Page 43 of 51

Display reads “No USB. Use menu to change modes”

- If you would like to connect to your device through a Bluetooth connection, simply open the Hub Menu, navigate to Mode, and select “MOUSE BT.” The LipSync will reset and there should no longer be any error messages.
- If you are trying to connect to your device through a wired USB connection:
- Check that the host device is powered on and ready to use.
- Check that the LipSync is securely plugged in on both ends of the USB cable.
- Make sure you are using a USB-C cable that transmits data, not a power-only cable.
- Try doing a LipSync Reset
- If the problem persists, contact support (see below).

Display shows error messages and enters safe mode

1. Disconnect the Hub from power.
2. Wait 15 seconds.
3. Unplug the LipSync Interface cable on both ends and plug both ends back in.
4. Reconnect the Hub to power.

If this does not resolve the error, make note of the error code on the Safe Mode menu screen, and refer to Table 2.

## USER GUIDE

Files available at www.github.com/makersmakingchange/LipSync | Page 44 of 51

### Error Codes

The LipSync automatically detects several hardware problems on startup. If an error is detected, a two-tone error sound will play and the device will go in to Safe Mode and display an error code. Table 2 lists the error codes and the corresponding actions to take as a user.

In some cases, a hardware error will be triggered when the power is disconnected and reconnected quickly. This can be resolved by disconnected the USB cable, waiting 30 seconds, and reconnecting the USB. If the problem persists, there might be a problem with the internal sensor or cable.

ERROR-007 can indicate that the LipSync Interface cable between the Hub and the Joystick is not connected properly. Disconnect the USB cable from the Hub, check both ends of the LipSync Interface Cable are securely attached, then reconnect the USB Cable to the Hub.

Table 2. LipSync Error Codes – User
Error Code | Connection Error | User Action Display | Ambient Pressure | Mouthpiece Pressure | Joystick Sensor
ERROR-001 | | | | ● | 1. Disconnect USB, wait 30 second, reconnect USB. 2. Contact support.
ERROR-002 | | | ●
ERROR-003 | | | ● | ●
ERROR-004 | | ●
ERROR-005 | | ● | | ●
ERROR-006 | | ● | ●
ERROR-007 | | ● | ● | ● | 1. Check that the LipSync interface cable is securely connected on both ends. 2. Confirm the LipSync Interface Cable is the right type. 3. Contact support
ERROR-008 | ● | | | ● | 1. Disconnect USB, wait 30 second, reconnect USB. 2. Contact support.
ERROR-009 | ● | | ●
ERROR-010 | ● | | ● | ●
ERROR-011 | ●
ERROR-012 | ● | ● | ● | ●
ERROR-013 | ● | ● | ●
ERROR-014 | ● | ●
ERROR-015 | ● | ● | ● | ●

## USER GUIDE

Files available at www.github.com/makersmakingchange/LipSync | Page 45 of 51

## Contacting Support

1. Contact the person who made the device.
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

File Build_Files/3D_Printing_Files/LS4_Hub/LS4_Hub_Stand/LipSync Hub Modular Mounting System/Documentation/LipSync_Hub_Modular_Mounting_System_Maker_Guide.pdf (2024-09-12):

V4.1| April 2024

## Modular Mounting System

## MAKER GUIDE

© 2024 by Neil Squire Society/Makers Making Change This work is licensed under the CC BY SA 4.0 License: http://creativecommons.org/licenses/by-sa/4.0
Files available at <Replace with MMC Github Link> | Page 1 of 9

### Overview

This document contains the necessary information to build the Modular Mounting System for the LipSync Hub.

### Contents

## MAKER GUIDE

Files available at <Replace with MMC Github Link> | Page 2 of 9
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

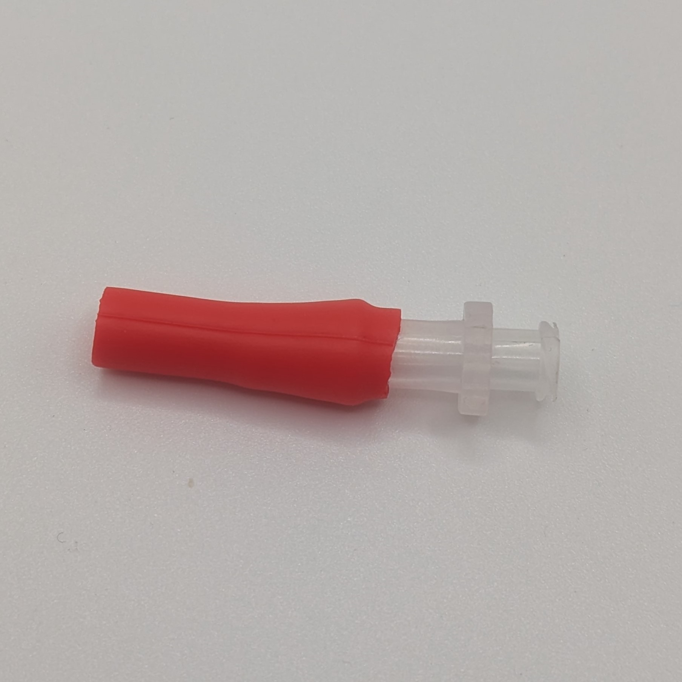
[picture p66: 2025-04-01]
Documentation/Working_Documents/Assets/Mouthpiece_Assembly/Mouthpiece_Tube_Assembled.jpg

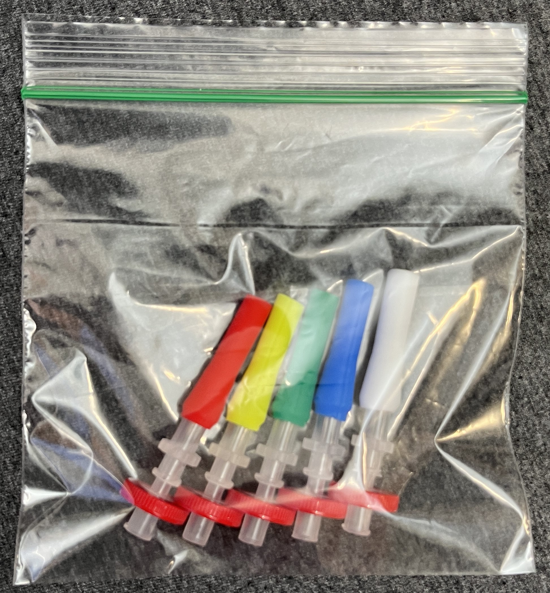
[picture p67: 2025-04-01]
Documentation/Working_Documents/Assets/Mouthpiece_Assembly/MouthpiecesBagged.JPG

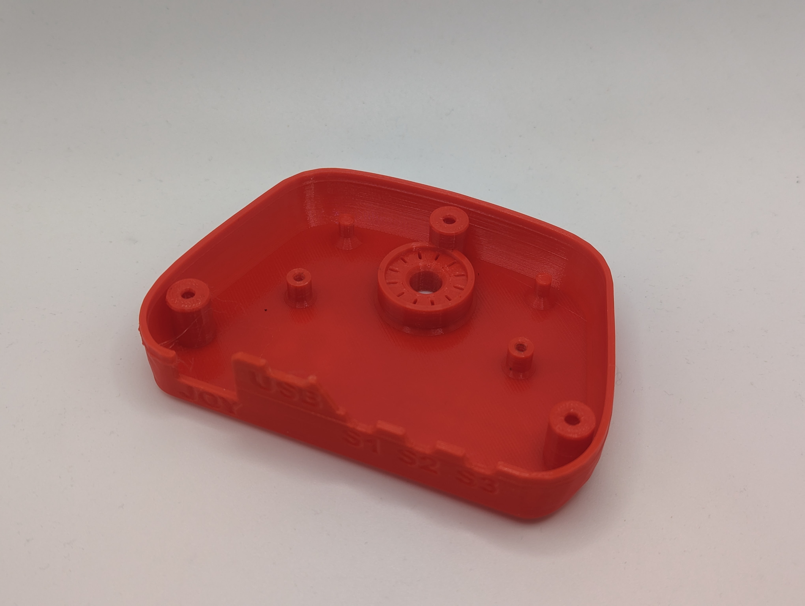
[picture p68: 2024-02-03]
Documentation/Working_Documents/Assets/Hub_assembly_Original/PXL_20240126_222539981.MP.jpg

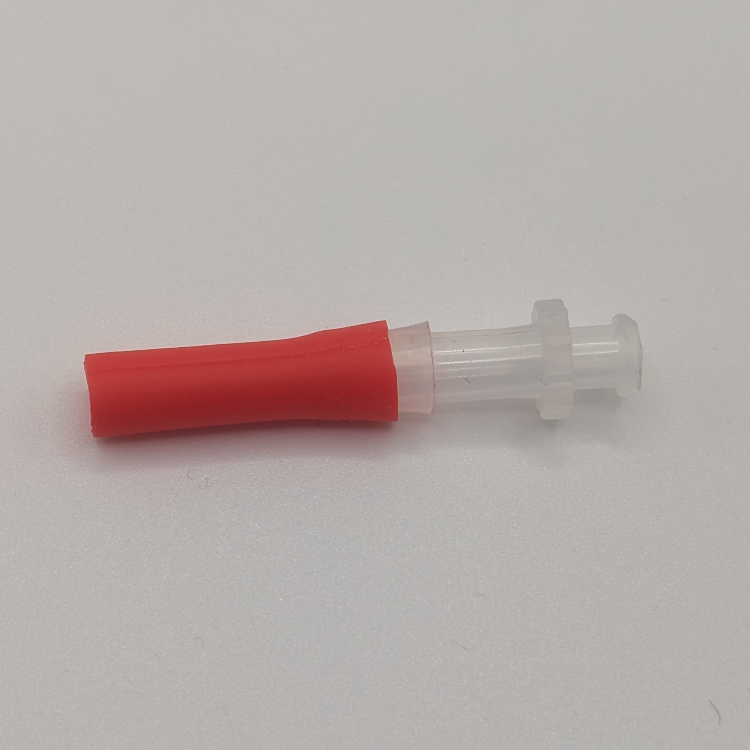
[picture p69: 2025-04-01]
Documentation/Working_Documents/Assets/Mouthpiece_Assembly/Mouthpiece_Tube_Assembly.jpg

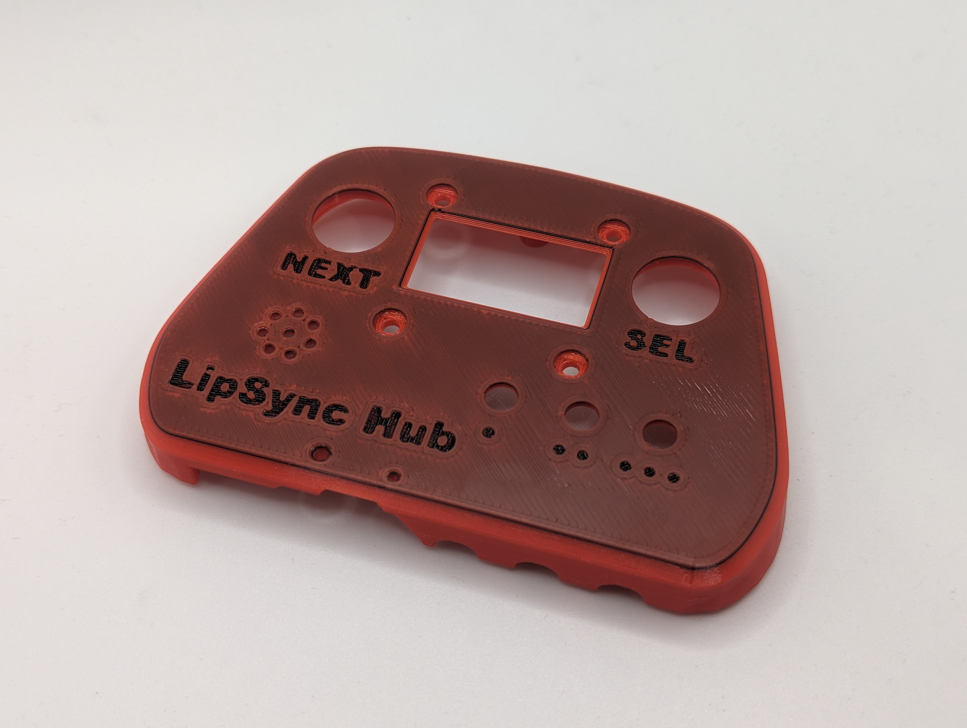
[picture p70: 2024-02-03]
Documentation/Working_Documents/Assets/Hub_assembly_Original/PXL_20240126_222555884.MP.jpg

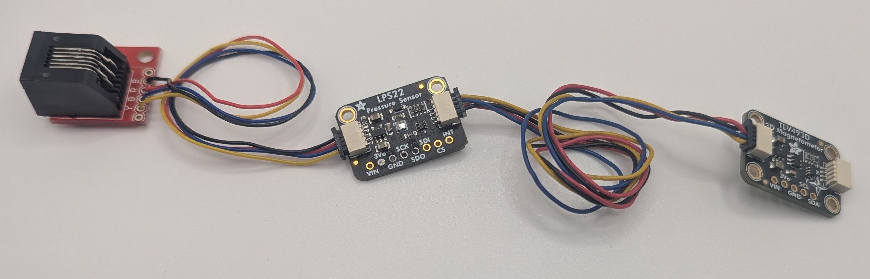
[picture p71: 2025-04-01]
Documentation/Working_Documents/Assets/Joystick_Assembly/RJ11_Ambient_Magnetic.jpg

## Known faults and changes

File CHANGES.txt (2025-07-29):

Version 4.1.1 | 2025-July-24
- Added CSV version of BOM to documentation folder to make it easier to see via GitHub
- Added copy of TLV493D-A1B6 library to repository
- Updated Maker Guide
  - Added instructions for manually adding TLV493D-A1B6 library
  - Added troubleshooting instructions for Seeeduino missing Python error
  - Added additional 3D printing instructions around tolerance and other processes

Version 4.1.0 | 2025-March-31
- Software bug fixes and added features 
	- TinyUSB Library bug fixed, now works with latest version (3.4.2) of the library
	- Full calibration changes
		- Moved to "More" menu to prevent Full Calibration from being selected when not necessary
		- Added warning message and confirmation page
		- Added error checking, if joystick was not moved enough during full calibration, use default value instead
	- No USB auto mode switch fix
		- 4.0.1 added a feature that if no USB was detected the LipSync would automatically switch to Bluetooth mode, but this caused unintentional effects 
		- Now, if no USB is detected, the screen displays an error message and buzzer plays an error tone, but continues to try to connect in the background
		- To change modes, the menu can now be used even if no USB is mounted.
	- i2c error checking
	- Light Brightness can now be adjusted through Hub menu or API
	- Scroll speed can now be adjusted through Hub menu
	- Scroll is now calculated differently, at a higher poll rate but not performed every loop, depending on the scroll speed
	- Fixed bug where scroll speed was dependent on cursor speed
	- Fixed bug in timers, so timer offset now works properly
	- Deadzone changes
		- Outer deadzone has its own variable and is independent of inner deadzone
		- Output now starts at 0% at the end of the innder deadzone, and goes to 100% at the edge of the outer deadzone
	- Added additional sounds for startup, powering off, and errors
	- Added watchdog implementation
	- Added safe mode accessible by Hub Buttons, or triggered during hardware error or watchdog
- Hardware changes
	- Ribs were added to the screw bosses on the LipSync Hub Top and LipSync Hub Bottom to increase strength
	- LipSync Mouthpiece was simplified
		- The updated mouthpiece is comprised of the same hydrophobic syringe filter, a Luer adapter, and a large silicone straw. This simplified design is easier to assemble, easier to clean, and has the added benefit of reducing the overall cost.
- Documentation updates
	- Maker Guide
		- TinyUSB library - can now use latest version (3.4.2)
		- Added additional assembly step to test joystick components before assembly into Joystick Gimbal and housing
	- User Guide
		- Updated to reflect changes to menu structure and full calibration process
		- Expanded troubleshooting with error messages
	- Created LipSync Firmware Upgrade Guide
	- Created LipSync Information Sheet

Version 4.0.2 | 2024-Dec-10
- Fixed bug related to sip and puff pressure calibration. 
	- Bug caused permanent sips or puffs if ambient pressure changed while sipping or puffing.

Version 4.0.1 | 2024-Apr-23
- Added instructions to use Tiny USB Library v2.3.0 to avoid startup error to Maker Guide.
- Software bug fixes 
	- Added timeout to menu screen
	- Added timeout to USB connection
	- Fixed lights bugs 

Version 4.0 | 2024-Feb-02
- Refined enclosure
- Full-featured firmware
	- USB Mouse, Wireless Mouse, USB Gamepad modes
	- Integrated display menu for settings adjustment
	- API settings adjustment
- Documentation released
	- User Guide
	- Maker Guide
	- Quickstart Guide
 	- BOM

Version 4.0.betaII | 2023-Dec-05
- Internal test build
	- prototype enclosures for Hub and Joystick units
- Basic mouse firmware
- Basic menu display
- Updated PCB layout
- Hub unit with feedback features
- joystick unit with sensors and rotational mounting

Version 4.0.beta | 2023-Nov-30
- Initial split architecture
	- PCB/microcontroller unit (Hub)
	- Joystick unit 
- Rebuilt 4 bearing gimbal
- Mouthpiece in-line with rotation center

Version 4.0.alphaII | 2022-Mar-31
- Full funcitonal system with magnet-based gimbal mechanism
- Enclosure with rotatable mounting feature
- Two-part custom PCB
- 3 neopixel LEDs for feedback
- 3 switch ports and on-device buttons for alterantive inputs
- User tested

Version 4.0.alphaI | 2021-Nov-30
- Initial gimbal-based magnetic joystick mechanism and sensor proof of concept
- 3 bearing gimbal
- Two-part custom PCB
- Mouthpiece axis offset from rotation axis

Version 3.0 - LipSync Classic | 2021-Sept-01
- Force sensitive resistor and spring based josytick
- Additional Bluetooth breakout board available to convert USB unit to wireless
- updated shell enclosure
- API settings adjustment
- Firmware settable mounting angle

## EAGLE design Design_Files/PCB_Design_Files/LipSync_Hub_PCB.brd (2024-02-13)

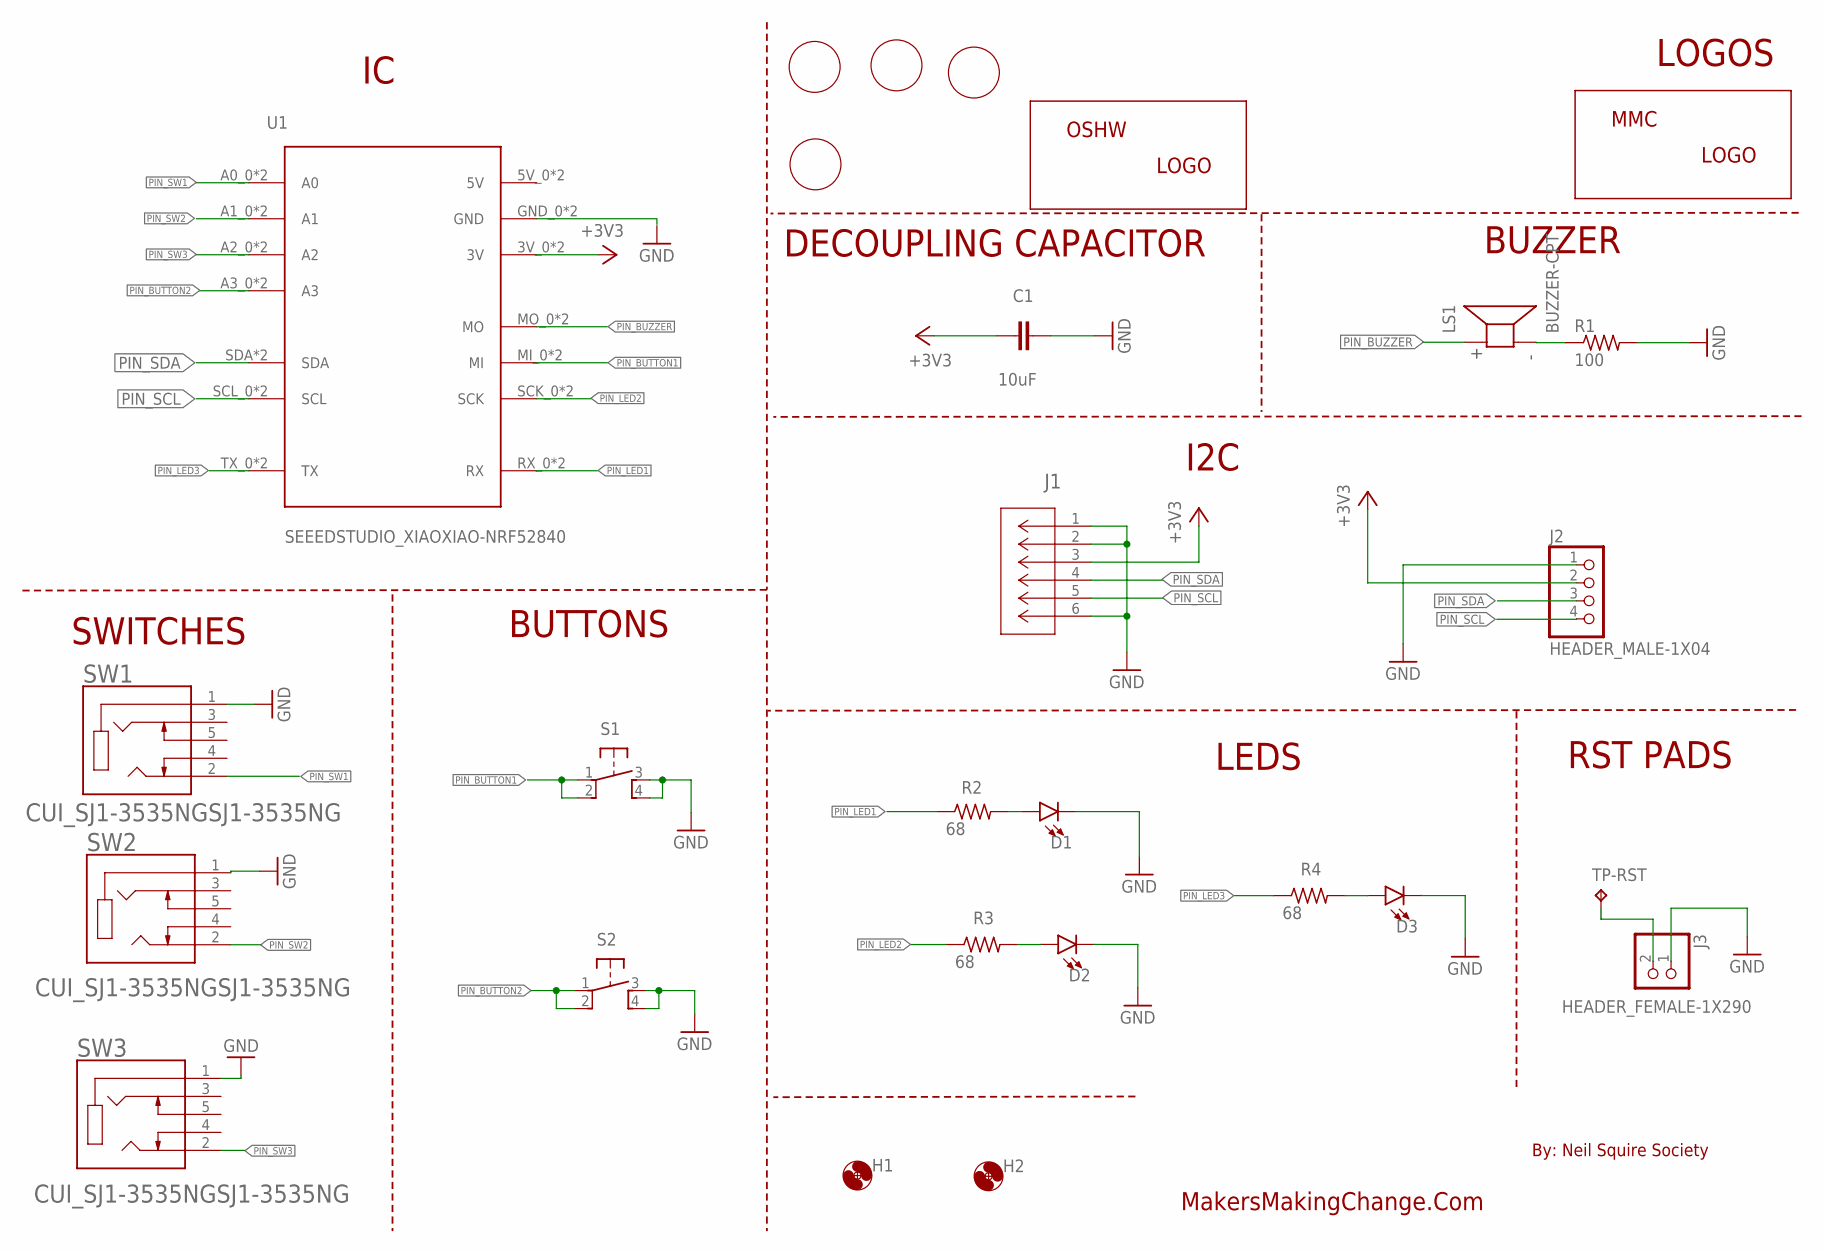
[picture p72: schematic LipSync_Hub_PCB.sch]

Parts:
C1: 10uF; CAP-050-030X075
D1, D2, D3: LED_5MM-5MM-RED-LONG; LED_5MM_RED_LONG
H1, H2: MOUNT-HOLE-3MM-CLEAR; HOLE-3MM-CLEAR
J1: 5555165-1; CONN6_5555165-1
J2: HEADER_MALE-1X04
J3: HEADER_FEMALE-1X290; HEADER_FEMALE-1X02_90
LOGO-BACK: MMC_LABEL-BACK; LABEL-BACK
LOGO-FRONT: MMC_LABEL-FRONT; LABEL-FRONT
LOGO-LIPSYNC-BACK: MMC_LABEL-LIPSYNC-X-LG; LABEL-LIPSYNC-X-LG
LOGO-MMC-BACK: MMC_LOGO-MD; MMC_MEDIUM_LOGO
LOGO-NORTH: MMC_LABEL-UP; LABEL-UP
LOGO-OSWH: OSHW_LOGO-SM; OSHW_SMALL_LOGO
LS1: BUZZER-CPT; CUI_CPT-1255C-090
R1: 100; RESISTOR_0205/7
R2, R3, R4: 68; RESISTOR_0205/7
S1, S2: SWITCH_OMRON-PTH-12; B3F-5050
SW1, SW2, SW3: CUI_SJ1-3535NGSJ1-3535NG; CUI_SJ1-3535NG
TP-RST: TESTPAD_TPB1,27; TESTPAD_B1,27
U1: SEEEDSTUDIO_XIAOXIAO-NRF52840; SEEEDSTUDIO_XIAO_NRF52840

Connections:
+3V3: C1.2, J1.3, J2.2, U1.3V_0 (3V), U1.3V_1 (3V)
GND: C1.1, D1.K (C), D2.K (C), D3.K (C), J1.1, J1.2, J1.6, J2.1, J3.1, R1.2, S1.3, S1.4, S2.3, S2.4, SW1.1, SW2.1, SW3.1, U1.GND_0 (GND), U1.GND_1 (GND)
unnamed: LS1.N, R1.1
unnamed: D2.A, R3.2
unnamed: J3.2, TP-RST.TP
unnamed: D3.A, R4.2
unnamed: D1.A, R2.2
PIN_BUTTON1: S1.1, S1.2, U1.MI_0 (MI), U1.MI_1 (MI)
PIN_BUTTON2: S2.1, S2.2, U1.A3_0 (A3), U1.A3_1 (A3)
PIN_BUZZER: LS1.P, U1.MO_0 (MO), U1.MO_1 (MO)
PIN_LED1: R2.1, U1.RX_0 (RX), U1.RX_1 (RX)
PIN_LED2: R3.1, U1.SCK_0 (SCK), U1.SCK_1 (SCK)
PIN_LED3: R4.1, U1.TX_0 (TX), U1.TX_1 (TX)
PIN_SCL: J1.5, J2.4, U1.SCL_0 (SCL), U1.SCL_1 (SCL)
PIN_SDA: J1.4, J2.3, U1.SDA, U1.SDA_0 (SDA)
PIN_SW1: SW1.2, U1.A0_0 (A0), U1.A0_1 (A0)
PIN_SW2: SW2.2, U1.A1_0 (A1), U1.A1_1 (A1)
PIN_SW3: SW3.2, U1.A2_0 (A2), U1.A2_1 (A2)

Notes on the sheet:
By: Neil Squire Society
MakersMakingChange.Com
SWITCHES
BUZZER
I2C
DECOUPLING CAPACITOR
LOGOS
BUTTONS
LEDS
RST PADS

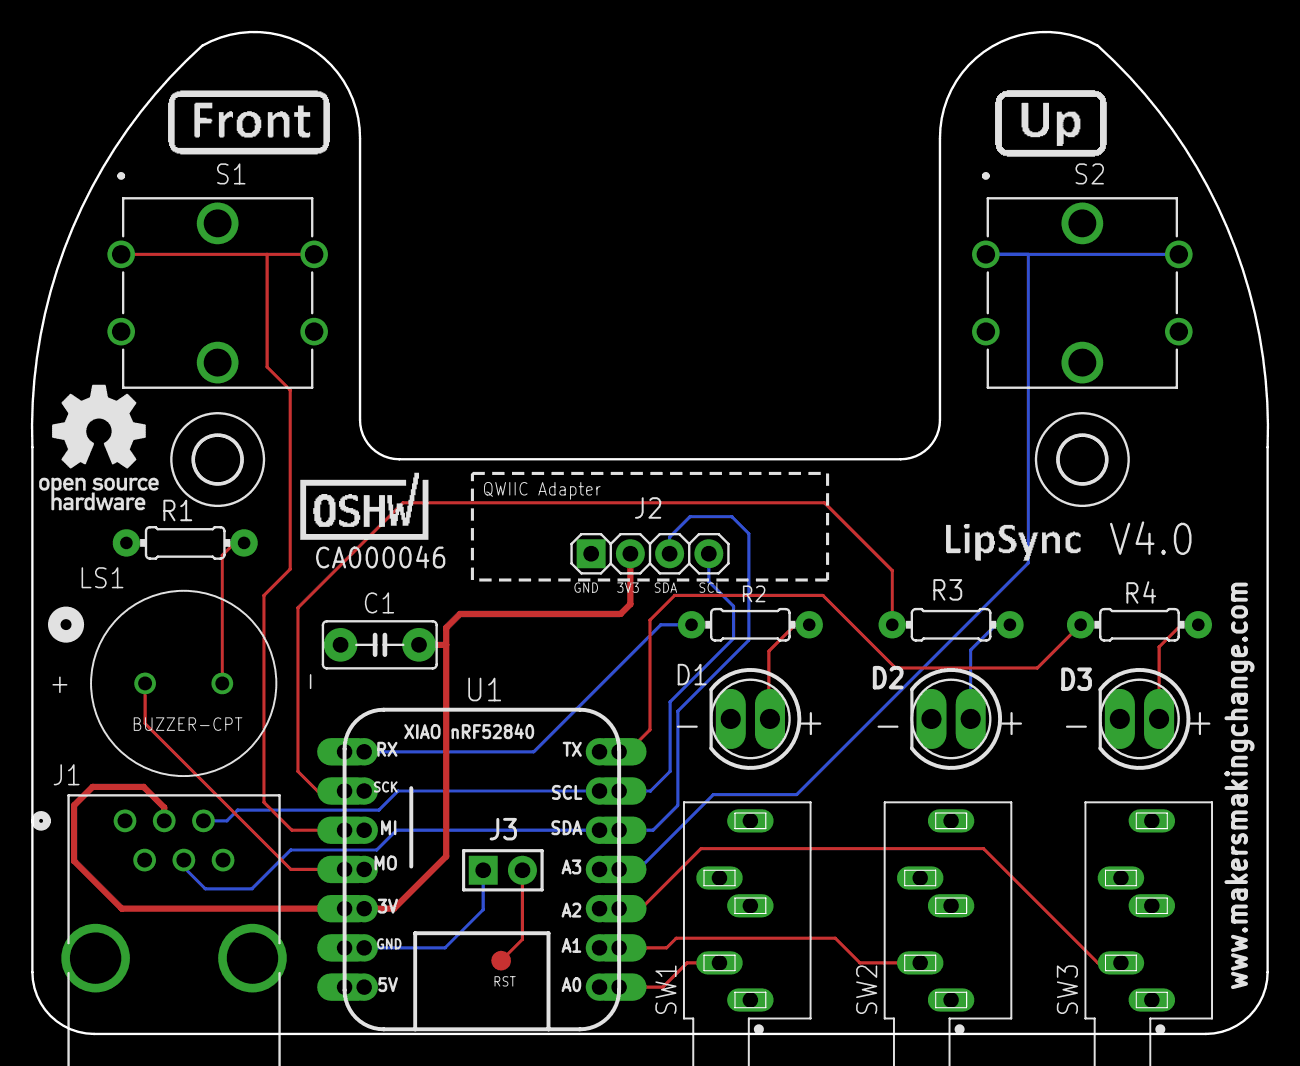
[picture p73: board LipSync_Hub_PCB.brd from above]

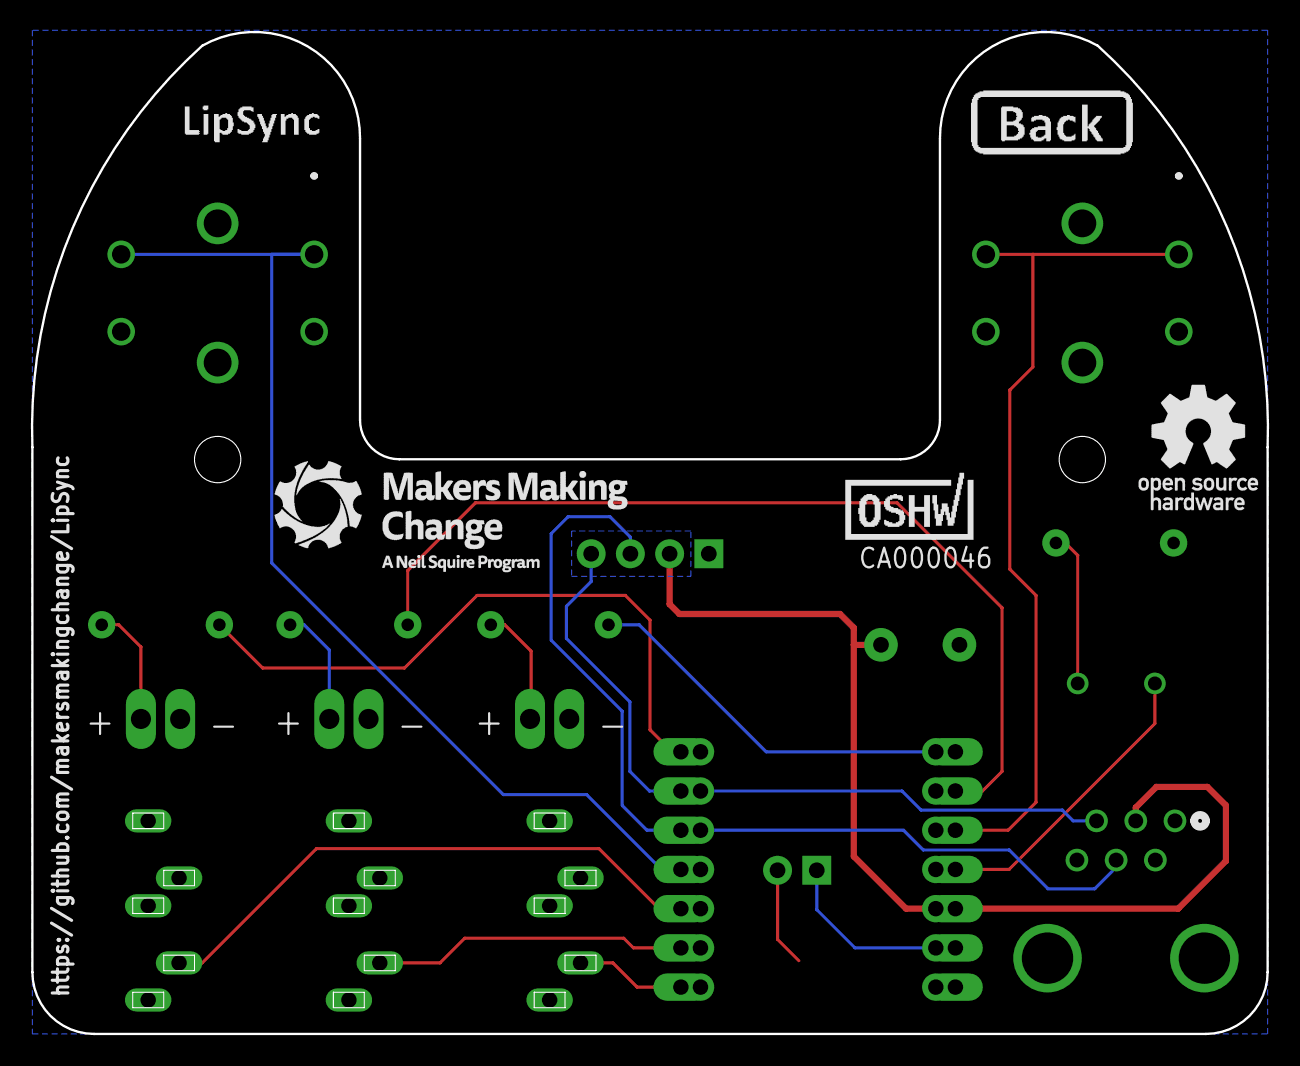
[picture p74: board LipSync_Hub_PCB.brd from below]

Board: 2 copper layers, 80.0 x 64.9 mm, 31 parts (5 on the bottom side), 18 nets.

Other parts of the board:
U$1: OSHW_SMALL_LOGO
U$2, U$4: CA000046; CERT-SMALL-SILK
U$3: LABEL-LIPSYNC-X-LG

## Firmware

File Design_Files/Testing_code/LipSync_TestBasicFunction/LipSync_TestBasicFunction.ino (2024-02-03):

/* 
* File: LipSync_TestBasicFunction.ino
* Firmware: LipSync
* Developed by: MakersMakingChange
* Version: 2023-Dec-11
* Copyright Neil Squire Society 2023. 
* License: GPL v3

  Copyright (C) 2023 Neil Squire Society
  This program is free software: you can redistribute it and/or modify it under the terms of
  the GNU General Public License as published by the Free Software Foundation,
  either version 3 of the License, or (at your option) any later version.
  This program is distributed in the hope that it will be useful, but WITHOUT ANY WARRANTY;
  without even the implied warranty of MERCHANTABILITY or FITNESS FOR A PARTICULAR PURPOSE.
  See the GNU General Public License for more details.
  You should have received a copy of the GNU General Public License along with this program.
  If not, see <http://www.gnu.org/licenses/>
*
* Summary: This code writes current state to serial port.
*/

#include <Tlv493d.h>  //Infinion TLV493 magnetic sensor
#include <Adafruit_LPS35HW.h>  // Sip and puff pressure sensor
#include <Adafruit_LPS2X.h> // Ambient pressure sensor


#define CONF_SWITCH1_PIN 0  // 3.5mm jack SW1
#define CONF_SWITCH2_PIN 1  // 3.5mm jack SW2
#define CONF_SWITCH3_PIN 2  // 3.5mm jack SW3


#define CONF_BUTTON_NEXT_PIN 9  // S1 MO Tactile next button
#define CONF_BUTTON_SEL_PIN 3    // S2 A3 Tactile select button

#define CONF_LED_MOUSE_PIN 8    // SCK
#define CONF_LED_GAMEPAD_PIN 7  // RX
#define CONF_LED_MOUSE_WIRELESS_PIN   6   //TX

#define CONF_BUZZER_PIN 10     // Buzzer 



Tlv493d Tlv493dSensor = Tlv493d();  // TLV493D Magenetic sensor object;
Adafruit_LPS35HW lps35hw = Adafruit_LPS35HW(); // Sip and puff pressure sensor object
Adafruit_LPS22 lps22; // Ambient pressure sensor
#define LPS22_I2CADDR 0x5C // Modified LPS22 address

float magnetic_x, magnetic_y, magnetic_z;

void setup() {
  Serial.begin(115200);

  while (!Serial) { delay(1); }  // Wait until serial port is opened

  Serial.println("Serial connection established");

  // Initiate Magnet Sensor
Tlv493dSensor.begin();
 Tlv493dSensor.setAccessMode(Tlv493dSensor.MASTERCONTROLLEDMODE); 
  // if (!Tlv493dSensor.begin()){
  //   Serial.println(F("Couldn't find TLV493D chip"));
  // }
  // else {
  //   Tlv493dSensor.setAccessMode(Tlv493dSensor.MASTERCONTROLLEDMODE);
  // }


  
  if (!lps35hw.begin_I2C()) {
    Serial.println(F("Couldn't find LPS35HW chip"));
  }


    // Try to initialize!
  if (!lps22.begin_I2C(LPS22_I2CADDR)) {
    Serial.println("Failed to find LPS22 chip");
    while (1) { delay(10); } // Hang on serial
  }
  Serial.println("LPS22 Found!");

  lps22.setDataRate(LPS22_RATE_25_HZ);
    switch (lps22.getDataRate()) {
    case LPS22_RATE_ONE_SHOT: Serial.println("One Shot / Power Down"); break;
    case LPS22_RATE_1_HZ: Serial.println("1 Hz"); break;
    case LPS22_RATE_10_HZ: Serial.println("10 Hz"); break;
    case LPS22_RATE_25_HZ: Serial.println("25 Hz"); break;
    case LPS22_RATE_50_HZ: Serial.println("50 Hz"); break;
    case LPS22_RATE_75_HZ: Serial.println("75 Hz"); break;
  }





  pinMode(CONF_SWITCH1_PIN, INPUT_PULLUP);
  pinMode(CONF_SWITCH2_PIN, INPUT_PULLUP);
  pinMode(CONF_SWITCH3_PIN, INPUT_PULLUP);

  pinMode(CONF_BUTTON_NEXT_PIN, INPUT_PULLUP);
  pinMode(CONF_BUTTON_SEL_PIN, INPUT_PULLUP);

  pinMode(CONF_LED_MOUSE_PIN, OUTPUT);
  pinMode(CONF_LED_MOUSE_WIRELESS_PIN, OUTPUT);
  pinMode(CONF_LED_GAMEPAD_PIN, OUTPUT);

  digitalWrite(CONF_LED_GAMEPAD_PIN, LOW);
  digitalWrite(CONF_LED_MOUSE_PIN, LOW);
  digitalWrite(CONF_LED_MOUSE_WIRELESS_PIN, LOW);
  
  digitalWrite(CONF_LED_GAMEPAD_PIN, HIGH);
  delay(1000);
  digitalWrite(CONF_LED_GAMEPAD_PIN, LOW);
  delay(1000);
  digitalWrite(CONF_LED_MOUSE_PIN, HIGH);
  delay(1000);
  digitalWrite(CONF_LED_MOUSE_PIN, LOW);
  delay(1000);
  digitalWrite(CONF_LED_MOUSE_WIRELESS_PIN, HIGH);
  delay(1000);
  digitalWrite(CONF_LED_MOUSE_WIRELESS_PIN, LOW);




}  // end setup

void loop() {

  bool inputStateSW1 = !digitalRead(CONF_SWITCH1_PIN);
  bool inputStateSW2 = !digitalRead(CONF_SWITCH2_PIN);
  bool inputStateSW3 = !digitalRead(CONF_SWITCH3_PIN);

  bool inputStateBN = !digitalRead(CONF_BUTTON_NEXT_PIN);
  bool inputStateBS = !digitalRead(CONF_BUTTON_SEL_PIN);

  int Tlv493dStatus = Tlv493dSensor.updateData();
  float magnetic_x = Tlv493dSensor.getX();
  float magnetic_y = Tlv493dSensor.getY();
  float magnetic_z = Tlv493dSensor.getZ();

  float tube_temperature = lps35hw.readTemperature(); // C
  float tube_pressure = lps35hw.readPressure(); // [hPa]

  sensors_event_t lps22_temp;
  sensors_event_t lps22_pressure;
  lps22.getEvent(&lps22_temp, &lps22_pressure);

  float ambient_temperature = lps22_temp.temperature;
  float ambient_pressure = lps22_pressure.pressure;



  Serial.print(Tlv493dStatus);
  Serial.print("\t");
  Serial.print(magnetic_x);
  Serial.print("\t");
  Serial.print(magnetic_y);
  Serial.print("\t");
  Serial.print(magnetic_z);
  Serial.print("\t");
  Serial.print(inputStateSW1);
  Serial.print("\t");
  Serial.print(inputStateSW2);
  Serial.print("\t");
  Serial.print(inputStateSW3);
  Serial.print("\t");
  Serial.print(inputStateBN);
  Serial.print("\t");
  Serial.print(inputStateBS);
  Serial.print("\t");
  Serial.print(tube_temperature);
  Serial.print("\t");
  Serial.print(tube_pressure);
  Serial.print("\t");
  Serial.print(ambient_temperature);
  Serial.print("\t");
  Serial.println(ambient_pressure);
  
  delay(50);



}  //end loop

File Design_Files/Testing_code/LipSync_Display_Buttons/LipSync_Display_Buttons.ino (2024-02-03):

/*******************
  This is an exmaple of the OLED screen menu for the LipSync
  Last edited: November 28, 2023
 *******************/

#include <SPI.h>
#include <Wire.h>
#include <Adafruit_GFX.h>
#include <Adafruit_SSD1306.h>

#define SCREEN_WIDTH 128 // OLED display width, in pixels
#define SCREEN_HEIGHT 64 // OLED display height, in pixels

#define OLED_RESET     -1 // Reset pin # (or -1 if sharing Arduino reset pin)
#define SCREEN_ADDRESS 0x3D ///< See datasheet for Address; 0x3D for 128x64, 0x3C for 128x32
Adafruit_SSD1306 display(SCREEN_WIDTH, SCREEN_HEIGHT, &Wire, OLED_RESET);

#define CONF_BUTTON2_PIN    3
#define CONF_BUTTON1_PIN   9

#define PIN_LED_MOUSE   8
#define PIN_LED_GAMEPAD 7
#define PIN_LED_MOUSE_WIRELESS  6

#define MAIN_MENU   0
#define EXIT_MENU   1
#define CALIB_MENU  2
#define MODE_MENU   3
#define CURSOR_SP_MENU   4
#define MORE_MENU    5
#define BLUETOOTH_MENU   6


//Calibration pages
#define CENTER_RESET_PAGE 11
#define FULL_CALIB_PAGE   12

//More Menus
#define SOUND_MENU        51
#define SIP_PUFF_MENU     52

#define MODE_MOUSE_USB  0
#define MODE_MOUSE_BT   1
#define MODE_GAMEPAD    2

#define SCROLL_DELAY_MILLIS   100

const int TEXT_ROWS = 4; //Probably a better way to do this with calculations based on text size and screen size

int currentMenu = 0;
int prevMenu = -1;
int currentSelection = 0;
int selectedLine; 

int mode = MODE_MOUSE_USB;
int tempMode = MODE_MOUSE_USB;
int cursorSpeedLevel = 5;
bool bluetoothOn = false;
bool soundOn = true;

bool scrollOn = false;
long scrollDelayTimer = millis();
int scrollPos = 12;

bool buttonSelPressed = false;
bool buttonNextPressed = false;
bool buttonSelPrevPressed = false;
bool buttonNextPrevPressed = false;

int cursorStart = 0;
int countMenuScroll = 0;

int currentMenuLength;
String *currentMenuText;
String selectedText;

String mainMenuText[5] = {"Exit Menu", "Calibrate", "Mode", "Cursor speed", "More"};
String exitConfirmText[4] = {"Exit", "settings?", "Confirm", "... Back"};
String calibMenuText[3] = {"Center reset", "Full Calibration", "... Back"};
String modeMenuText[4] = {"MOUSE USB", "MOUSE BT", "GAMEPAD ", "... Back"};
String modeConfirmText[4] = {"Change", "mode?", "Confirm", "... Back"};
String cursorSpMenuText[4] = {"  ", "Increase", "Decrease", "... Back"};
String bluetoothMenuText[4] = {"Bluetooth:", "<>", "Turn <>", "... Back"};
String moreMenuText[4] = {"Sound", "Sip & Puff", "... Back", "         "};
String soundMenuText[4] = {"Sound:", "<>", "Turn <>", "... Back"};
String sipPuffThreshMenuText[4] = {"Sip Threshold", "Puff Threshold", "... Back"};

// Number of selectable options in each menu
const int mainMenuLen = 5;
const int exitConfirmLen = 2;
const int calibMenuLen = 3;
const int modeMenuLen = 4;
const int cursorSpMenuLen = 3;
const int bluetoothMenuLen = 2;
const int moreMenuLen = 3;
const int soundMenuLen = 2;
const int sipPuffThreshMenuLen = 3;

void setup() {
  pinMode(CONF_BUTTON2_PIN, INPUT_PULLUP);
  pinMode(CONF_BUTTON1_PIN, INPUT_PULLUP);

  pinMode(PIN_LED_MOUSE, OUTPUT);
  pinMode(PIN_LED_GAMEPAD, OUTPUT);
  digitalWrite(PIN_LED_MOUSE, LOW);
  digitalWrite(PIN_LED_GAMEPAD, LOW);

  Serial.begin(115200);

  switch (mode){
    case MODE_MOUSE_USB:
      digitalWrite(PIN_LED_GAMEPAD, LOW);
      digitalWrite(PIN_LED_MOUSE, HIGH);
      break;
    case MODE_MOUSE_BT:
      digitalWrite(PIN_LED_GAMEPAD, LOW);
      digitalWrite(PIN_LED_MOUSE, HIGH);
      break;
    case MODE_GAMEPAD:
      digitalWrite(PIN_LED_MOUSE, LOW);
      digitalWrite(PIN_LED_GAMEPAD, HIGH);
      break;
  }
  
  delay(500); // Start up delay so screen is ready to write to

  // SSD1306_SWITCHCAPVCC = generate display voltage from 3.3V internally
  if (!display.begin(SSD1306_SWITCHCAPVCC, SCREEN_ADDRESS)) {
    Serial.println(F("SSD1306 allocation failed"));
    for (;;); // Don't proceed, loop forever
  }
  
  display.clearDisplay();
  display.setTextWrap(false);
  display.display();

  //Start on main menu
  currentMenu = MAIN_MENU;
  mainMenu();

}

void loop() {
  // put your main code here, to run repeatedly:

  // read switches
  readButtons();

  buttonActions();

  prevMenu = currentMenu;

  if (scrollOn){
    scrollLongText();
  }

}

void initDisplay() {
  display.clearDisplay();

  display.setTextSize(2);                                   // 2x scale text
  display.setTextColor(SSD1306_WHITE, SSD1306_BLACK);       // Draw white text on solid black background

  display.setCursor(0, 0);
}

void displayMenu() {

  initDisplay();

  for (int i = 0; i < TEXT_ROWS; i++) {
    if (i >= cursorStart){
      display.print(" "), display.println(currentMenuText[i+countMenuScroll]);
    } else {
      display.println(currentMenuText[i]);
    }
  }

  display.display();

  //currentSelection = 0;
  displayCursor();
}

void displayCursor(void) {
  int cursorPos;
  if (currentSelection + cursorStart > TEXT_ROWS-1){
    cursorPos = TEXT_ROWS-1;
  } else {
    cursorPos = currentSelection;
  }

  display.setTextSize(2);                                   // 2x scale text
  display.setTextColor(SSD1306_WHITE, SSD1306_BLACK);       // Draw white text on solid black background

  // Show cursor on text line of selection index, erase previous cursor
  display.setCursor(0, 16 * cursorStart);  
  for (int i = 0; i < currentMenuLength; i++) {    
    if (i == cursorPos) {
      display.println(">");
    } else {
      display.println(" ");
    }
  }

  display.display();

  selectedLine = cursorStart + currentSelection;
  selectedText = currentMenuText[selectedLine];
  
  if (selectedText.length() > 9){
    scrollOn = true;
    scrollPos = 12;
    delay(200);                           // may need to remove this
    scrollLongText();
  } else {
    scrollOn = false;
  }
}

void nextSelection(void) {
  if (scrollOn){
    display.setCursor(0, selectedLine *16);
    display.print("                                   ");
    display.setCursor(12, selectedLine *16);
    display.print(selectedText);
  }

  currentSelection++;
  if (currentSelection >= currentMenuLength) {   
    currentSelection = 0;
    countMenuScroll = 0;
    //cursorPos = currentSelection;
    displayMenu();
  } else if (currentSelection + cursorStart > TEXT_ROWS-1){
    countMenuScroll++;
    displayMenu();
  } 

  displayCursor();

}


void scrollLongText(void){
  int minPos = -12 * selectedText.length();
  
  display.setTextSize(2);                                   // 2x scale text
  display.setTextColor(SSD1306_WHITE, SSD1306_BLACK);       // Draw white text on solid black background
  display.setTextWrap(false);
  
  if (millis() - scrollDelayTimer >= SCROLL_DELAY_MILLIS){
    scrollDelayTimer = millis();
    
    //Clear previous text by writing over it with blank text
    display.setCursor(0, selectedLine *16);
    display.print("                                   ");

    //Display text in new position to simulate scrolling
    display.setCursor(scrollPos, selectedLine *16);
    display.print(selectedText);

    display.setCursor(0, selectedLine *16);
    display.print(">");
    display.display();
    //displayCursor();
    scrollPos = scrollPos-4;
    if (scrollPos < minPos) scrollPos = display.width();
  }
  
}

void readButtons(void){
  buttonSelPrevPressed = buttonSelPressed;
  buttonNextPrevPressed = buttonNextPressed;

  buttonSelPressed = !digitalRead(CONF_BUTTON2_PIN);
  buttonNextPressed = !digitalRead(CONF_BUTTON1_PIN);
}

void buttonActions(void){
  inputNext();
  inputSelect();
}

void inputNext(void){
    // Move this to general loop? 
  if (buttonNextPressed){
    //start timer to determine long press
  } else if (buttonNextPrevPressed){          // when button is released
    nextSelection();
  }
}
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

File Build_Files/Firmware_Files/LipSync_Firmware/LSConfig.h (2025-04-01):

/* 
* File: LSConfig.h
* Firmware: LipSync
* Developed by: MakersMakingChange
* Version: v4.1 (28 March 2025)
  License: GPL v3.0 or later

  Copyright (C) 2024 - 2025 Neil Squire Society
  This program is free software: you can redistribute it and/or modify it under the terms of
  the GNU General Public License as published by the Free Software Foundation,
  either version 3 of the License, or (at your option) any later version.
  This program is distributed in the hope that it will be useful, but WITHOUT ANY WARRANTY;
  without even the implied warranty of MERCHANTABILITY or FITNESS FOR A PARTICULAR PURPOSE.
  See the GNU General Public License for more details.
  You should have received a copy of the GNU General Public License along with this program.
  If not, see <http://www.gnu.org/licenses/>

*/

#include "LSUtils.h"

// Debugging
#define USB_DEBUG  0 // Set this to 0 for best performance
#define SHOW_CONNECTION_TIME 0 // Set to 0 for production

#define CONF_ENABLE_WATCHDOG 1 // Set to 1 to enable hardware watchdog

//***DO NOT CHANGE***//
#define CONF_LIPSYNC_MODEL 1                // 1: Lipsync w/ Hub

#define CONF_LIPSYNC_VERSION_MAJOR  4
#define CONF_LIPSYNC_VERSION_MINOR  1
#define CONF_LIPSYNC_VERSION_REV  0

const String CONF_LIPSYNC_VERSION_STRING = String(CONF_LIPSYNC_VERSION_MAJOR) + "." + String(CONF_LIPSYNC_VERSION_MINOR) + "." + String(CONF_LIPSYNC_VERSION_REV);

// I2C Devices
#define I2CADDR_DISPLAY 0x3D  // Display address (61)
#define I2CADDR_LPS22   0x5C  // Modified LPS22 address (92)
#define I2CADDR_LPS35HW 0x5D  // LPS35HW address (93)
#define I2CADDR_TLV493D 0x5E  // 3D Hall Effect Sensor (94)
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

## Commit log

2022-01-10 Fixed pressure sensor bug causing it stop responding
2022-01-11 Fixed compensation pressure bug
2022-01-13 Added joystick calibration
2022-01-20 replaced scheduler with mills timer
2022-01-27 Changed led structure to use timer! TODO: Fix non static function call
2022-01-30 Updated the pressure class to include sap state logic calculation
2022-01-31 Added updated led output based on timers
2022-02-03 Added state logic to led actions
2022-02-08 Added timer implementation of calibration process and fixed bugs
2022-02-08 Testing bluetooth led
2022-02-11 Fixed bug: Device doesn't mount on battery or simple power source.
2022-02-17 Fixed change speed led bugs
2022-02-18 Added pressure mode change API
    Added pressure mode change API
2022-03-01 Update LSPressure.h
    Move onboard pressure sensor begin within mode flag so device doesn't hang.
2022-03-02 Added comments to pressure class
2022-03-03 Testing reference pressure update after each sip and puff release
2022-03-04 Updated calibration point saving process ( Store raw values instead of centered points )
2022-04-02 Resolved centering bug after calibration
2022-04-05 Testing simple low-pass filter
2022-04-06 Added input deadzone in mT and improved low-pass filter
2022-04-08 Added white LED Colour
2022-04-10 Updated Speed control LED Feedback
2022-04-12 Updated calibration steps
2022-04-13 Fixed _inputRadius bug and optimized calibration process
2022-04-14 Added bluetooth scan LED feedback
2022-07-15 Alpha II - Closed Beta Publish
    [Adafruit Feather nRF52840 Sense.brd, Adafruit Feather nRF52840 Sense.sch, Adafruit LPS35HW.brd, Adafruit LPS35HW.sch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]
2023-11-20 Update LSPressure.h
    Replace BMP sensor with LPS22
2023-11-20 Update LSConfig.h
    Add Beta pin configurations
2023-11-20 Update LSOutput.h
    Disable Neopixel LEDs
2023-11-21 Update LSPressure.h
    Fix LPS22 pressure sensor code
2023-11-23 Change default calibration to +-30
2023-11-24 Update LSBLE.h
    Update Bluetooth device name to LipSync X
2023-11-24 Update LSJoystick.h
    Update angles for new sensor orientation
2023-11-24 Update LSPressure.h
    Fix LPS22 pressure reading
2023-11-29 Update LSOutput.h
    Update LEDs
2023-11-29 Update LSAPI.ino
    Get pressure value returns all pressures.
2023-12-11 Updated pins for new PCB
2023-12-13 Update LSConfig.h
    Fix LED pin numbering
2024-01-03 Added display startup screen
    Added text that appears when the LipSync is powered on.
2024-01-19 Added temporary print statements and delays for troubleshooting wireless
2024-01-22 Update LED code
    -change mode based leds to directional (i.e. left,middle,right)
    -update total number of LEDs
2024-01-23 Squashed commit of the following:
    commit 7c8e3c8e380d82a9eb80000ba14a30034dce5712
    Author: jversloot <50920198+jversloot@users.noreply.github.com>
    Date: Tue Jan 23 11:29:09 2024 -0400
    Fixed mode changes
    commit 7e81b2833a8864a2ef7bc5002c542df4dcdea19b
    Author: jversloot <50920198+jversloot@users.noreply.github.com>
    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
2024-01-23 Changed title of device for USB and Bluetooth
    Removed X
2024-01-24 Fixed timing of center reset calibration screen prompts
2024-01-24 Added full calibration prompts
2024-01-24 Reworded full calibration prompts
2024-01-24 Squashed commit of the following:
    commit 68e7c99d0d5a11f0bae447e74e74b3b028b48732
    Date: Wed Jan 24 17:07:07 2024 -0400
    Center reset now triggers startup noise and Center Reset Complete page
    commit fe7315b0337279dcc387c1d0f1a15b084c2122ea
    Date: Wed Jan 24 15:10:57 2024 -0400
    Reworded full calibration prompts
    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
2024-01-24 Removed unneeded Serial print statements
2024-01-24 Updated default values for full extents to match current design
2024-01-24 Light Update
    corrected pin mapping
    added light test
    added actions to LED struct
2024-01-24 Squashed commit of the following:
    commit 54c3aa7eed507ad014a13c1c80f4aa6799c7f14b
    Date: Wed Jan 24 18:10:52 2024 -0400
    Updated default values for full extents to match current design
    commit aae6c582d858a4612ec0af446fea291cca5a156d
    Date: Wed Jan 24 17:51:15 2024 -0400
    Removed unneeded Serial print statements
    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
2024-01-24 Update LSTest.ino
    Expand LED test to include Micro LED
2024-01-25 Move mapping to LSConfig.h
    Moved ledActionProperty, switchActionProperty, buttonActionProperty, and sapActionProperty to LSConfig.h
2024-01-25 Fixed bug in mode menu
    Fixed bug where current mode would become un-highlighted if you circled through the menu
2024-01-25 Cleaned up repeated variable and changed Bluetooth device name
2024-01-25 Added tones to full calibration
2024-02-03 Clean-out Alpha II
    [Buttons.stl, Front Enclosure.stl, LED Cover.stl, LED_Bending_Jig v2.stl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]
2024-02-03 Add V4.0 print files
    [LS4_Front_Cap.stl, LS4_Gimbal_Shield.stl, LS4_Gimbal_Sled.stl, LS4_Hub_Bottom.stl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]
2024-02-03 Add V4.0 PCB Build files
2024-02-03 Add v4.0 PCB files
    [LipSync_Hub_PCB.brd, LipSync_Hub_PCB.sch]
2024-02-03 Remove 3rd party PCB files
    [Adafruit Feather nRF52840 Sense.brd, Adafruit Feather nRF52840 Sense.sch, Adafruit LPS35HW.brd, Adafruit LPS35HW.sch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]
2024-02-10 Add Open Source Hardware Certification
    Add Open Source Hardware information to readme and PCB
    Add license graphic
    Update PCB Build Files
    [LipSync_Hub_PCB.brd]
2024-02-21 Update LS4_Hub_Top.stl
    Fix print orientation
    [LS4_Hub_Top.stl]
2024-04-24 Update LSConfig.h
    -renumber CONF_ACTIONS to fix LED mapping
2024-04-24 Update LSConfig.h
    Fix up LED action mapping
2024-04-25 Fixed bug
    Joystick now does not move until calibration is complete (on startup and during full calibration)
2024-04-25 Fixed colours of onboard LED for operating mode
2024-05-01 Update LSMemory.h
    Change from DynamicJsonDocument to JsonDocument to upgrade ArduinoJson 6 to 7
    https://arduinojson.org/v7/how-to/upgrade-from-v6/
2024-05-01 Update LSMemory.h
    Update ArduinoJson for now obsolete createdNestedArray()
    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
2024-05-09 Add additional internal files.
    [LipSync_Logo.dxf]
2024-09-12 Added printable hub stand files
    [Adaptor Pin.stl, Arm 90 Straight QuarterTwenty LowPoly v5.f3d, Base Low Poly v4.f3d, LS4_Hub_Stand_Front.stl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]
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2025-01-10 Added error handling to full calibration
    If corner cal values are too small, use default values instead
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2025-01-21 Update LSConfig.h
    Remove LED_STATE_OFF and LED_STATE_ON to avoid compiler error
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2025-01-25 Fix LED brightness and clean up code
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2025-01-27 Separate i2c and cable error pages; sounds tweaks
2025-01-27 Fixed LED blink bug
    Fixed LED blink bug due to timer indexing
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2025-02-03 Update LipSync_Firmware.ino
    Fixed indexing for calibration timer
2025-02-03 Update LipSync_Firmware.ino
    Fixed full calibration default polarity
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2025-02-07 Fixed sip and puff bug
    Fixed bug where sip and puff didn't work initially after powering on. Added 20 ms delay to LSPressure::begin
2025-02-14 Fixed bug with timers not incrementing properly
    Moved where timers were being incremented so they would run the correct number of times and then delete the timer. Also reformatted the switch case to a shorter if statement.
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2025-02-24 Fix offset pressure timeout
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2025-02-26 Update LipSync_Firmware.ino
    Fix serial print statement
2025-02-28 Update scroll poll rate and fix scroll screen display
    Scroll adjustment in the menu now checks scroll level before displaying, in case it was not successful, such as setting to level 11
2025-03-05 Longer cable error screen
    Longer cable error screen to give time to read the longer message
2025-03-05 Replace hardcoded led brightness with variable
    - Also altered the LED brightness level to output equation
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2025-03-06 Update LSConfig.h
    Fixed bug where mode LED did not light up after closing menu
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2025-03-14 Update Hub files with reinforced screw bosses
    Ribs were added to screw bosses in the Hub to add additional strength
    [LS4_Hub_Bottom.stl, LS4_Hub_Top.stl]
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2025-03-18 Update LSPressure.h
    Add linebreak to pressure sensor timeout error message
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2025-03-21 Fix case
2025-03-21 Update LipSync_Firmware.ino
    Fixed missing bracket
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2025-04-01 Add updated documentation
    [LipSync_BOM.csv, LipSync_BOM.xlsx]
2025-04-10 Add Update About MMC GitHub Action
    [Adaptor Pin.stl, Arm 90 Straight QuarterTwenty LowPoly v5.f3d, Base Low Poly v4.f3d, LS4_Front_Cap.stl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]
2025-04-11 Revert "Merge pull request #57 from makersmakingchange/add-update-about-mmc-github-action"
    This reverts commit 1f6c27cabff471b88226f12394d6ccfcc4c094f4, reversing
    changes made to e15e4f23ab8dd0b5a3136821ad79306b5be22cec.
    [Adaptor Pin.stl, Arm 90 Straight QuarterTwenty LowPoly v5.f3d, Base Low Poly v4.f3d, LS4_Front_Cap.stl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]
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2025-07-21 Re-add LipSync BOM
    [LipSync_BOM.csv]
2025-07-29 Update Maker Guide
    Include instruction about manually adding library.
    Add instructions about python error
    Add instructions about using FFF for 3d printed parts.

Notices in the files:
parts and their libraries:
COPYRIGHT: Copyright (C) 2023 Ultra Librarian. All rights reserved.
